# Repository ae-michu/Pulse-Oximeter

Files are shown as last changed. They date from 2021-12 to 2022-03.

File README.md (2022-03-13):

# Pulse-Oximeter
Handheld, battery powered device for measuring heart BPM and blood-oxygen content with full custom PCB design, interface design and housing.

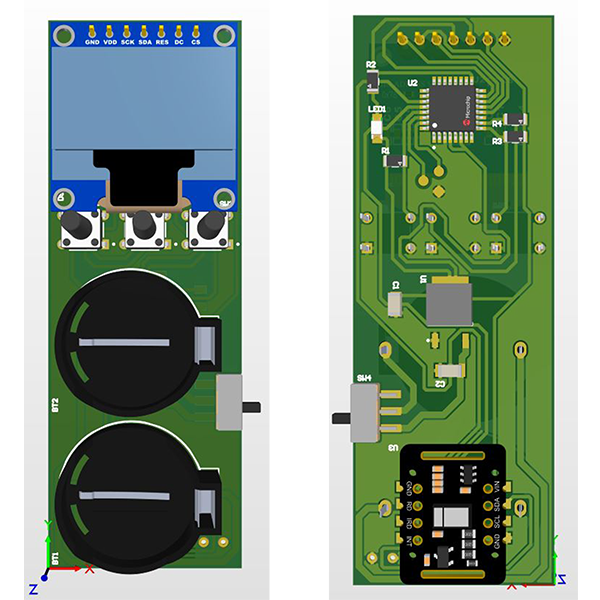
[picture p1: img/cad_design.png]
PCB CAD Design


## Introduction
It was created as a team project for a microprocessor controllers class at our university. The goal was to create a device that utilizes microcontrollers and at least 3 built-in interfaces.

## Parameters
* 3.3V power, by using two CR2032 coin cell batteries
* ATMega328p-AU with internal 8MHz clock
* MAX30102 I2C Sensor for measuring bpms and blood-oxygen levels
* 0.96" OLED SPI Display

## Working principles (and design choices)

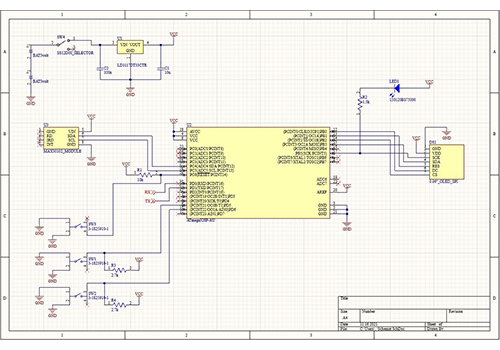
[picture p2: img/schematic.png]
Electrical schematic


### Power
Device is powered by two 3V CR2032 batteries connected in series. To sustain 3.3V the batteries were connected to LD1117-3.3 fixed voltage reagulator.

### Bootloader
Due to 3.3V power supply and according to the documentation the chips oscillator had to be lowered from 16Mhz to 8Mhz. To save space on the PCB and also lower the cost of the device we choose to flash a new bootlader that enabled the internal 8Mhz oscillator.

### BPM measurement
To achieve fast readouts and not compromise accuracy we chose to increase the amount of samples (used to calculate the moving average) with time. This gives us very fast printout of the first readings and increases accuracy with the time of measurement.

### Splash screen animation
To add some life to our interface we decided to add a splash screen animation that plays everytime the device is turned on. Each frame of the animation is stored as a bitmap. Unfortunately loading all frames from program memory caused long boot time after the device was turned off for a while (week).

### PCB
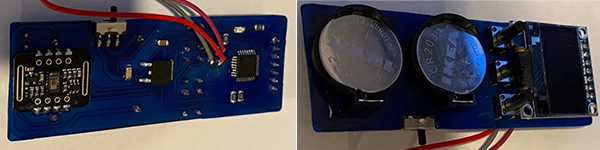
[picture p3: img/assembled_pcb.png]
Assembled PCB


It wasn't in the requirements for the project but we decided to create a pcb for the device which allowed us to use SMD components and minify the size of the product. It was designed using Altium Designer and home-etched using B327 eatching solution. Toner transfer, before etching, was done using a solution of 70% rubbing alcohol and 30% acetone. To avoid solder briding and shorts uv curable solder mask was also put on.

### Enclousure
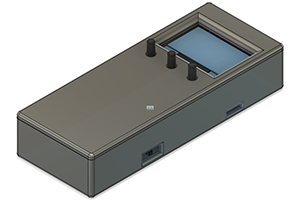
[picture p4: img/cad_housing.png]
Housing


Enclousure was designed in Fusion 360 and 3D printed using white PLA fillament. It was desinged around CAD files of the pcb.

## Team
<table>
<td align="center"><a href="https://github.com/ae-michu"><br /><sub><b>Michał Pękal</b></sub></a><br /><p style="font-size:12px">Electronics Design<br> Firmware</p></td>

<td align="center"><a href="https://github.com/olafka0"><br /><sub><b>Oliwia Wawrzyniak</b></sub></a><br /><p style="font-size:12px">UX/UI Design<br><br></p></td>

<td align="center"><a href="https://github.com/pablithone"><br /><sub><b>Paweł Lewandowski</b></sub></a><br /><p style="font-size:12px">Enclousure Design<br><br></p></td>
</table>

<br>
<br>
<br>

### Legal note
THE SOFTWARE, HARDWARE DESIGN ARE PROVIDED “AS IS”, WITHOUT WARRANTY OF ANY KIND, EXPRESS OR IMPLIED, INCLUDING BUT NOT LIMITED TO THE WARRANTIES OF MERCHANTABILITY, FITNESS FOR A PARTICULAR PURPOSE AND NONINFRINGEMENT. IN NO EVENT SHALL THE AUTHORS OR COPYRIGHT HOLDERS BE LIABLE FOR ANY CLAIM, DAMAGES OR OTHER LIABILITY, WHETHER IN AN ACTION OF CONTRACT, TORT OR OTHERWISE, ARISING FROM, OUT OF OR IN CONNECTION WITH THE SOFTWARE AND HARDWARE DESIGN OR THE USE OR OTHER DEALINGS IN THE SOFTWARE AND HARDWARE DESIGN.

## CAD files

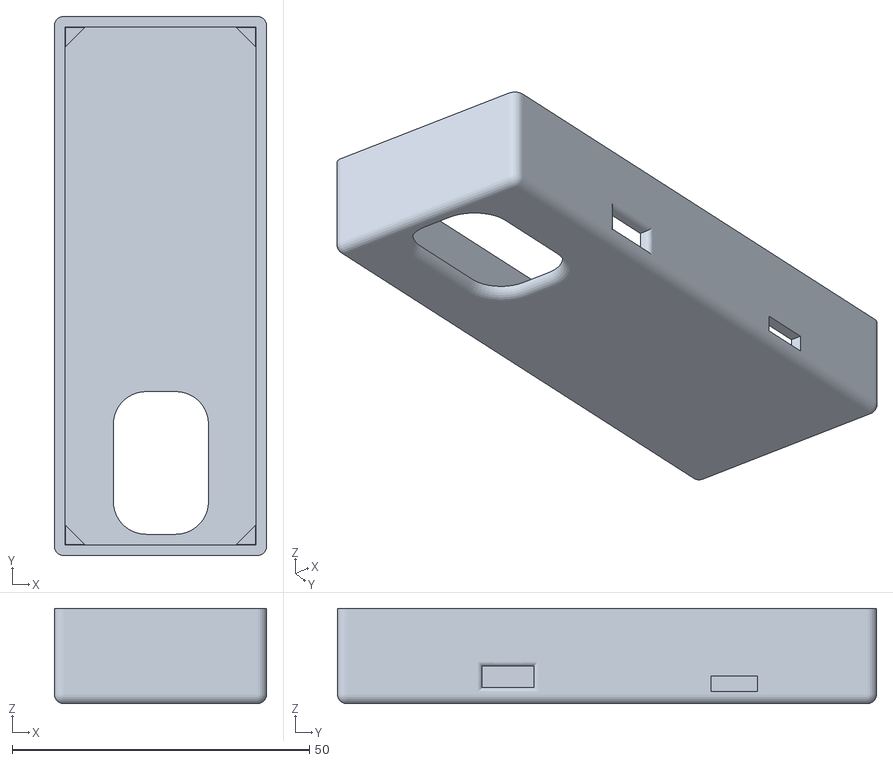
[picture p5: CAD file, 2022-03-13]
CAD/housing/main_housing.stl
35.7 x 90.7 x 16.0

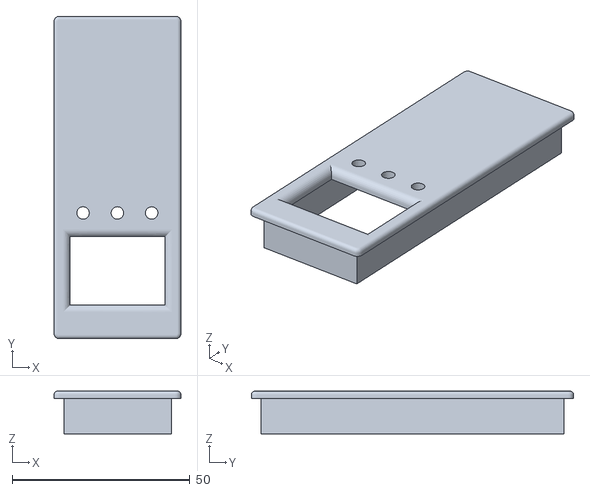
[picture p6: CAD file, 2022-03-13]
CAD/housing/top_cover.stl
35.7 x 90.6 x 12.0

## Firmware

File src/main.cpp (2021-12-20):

#include <Arduino.h>
#include <display.h>
#include <sensor.h>

// #define DEBUG                    // uncomment to enable writing data to monitor

#define BUTTON1         5           // pin number of first button (bpm)
#define BUTTON2         6           // pin number of second button (o2)

#define DISPLAY_DC      8           // pin number od display dc pin
#define DISPLAY_CS      10          // pin number of display cs pin
#define DISPLAY_RESET   9           // pin number of display reset pin

// init display and sensor objects
Display display(U8G2_R0, DISPLAY_CS, DISPLAY_DC, DISPLAY_RESET);
Sensor sensor;

// set global variables
bool screen = false;              // false - bpm screen, true - o2 screen
bool changeScreenFlag = true;     // false when screen change should occur
int lastBpm = 0;                  // store last bpm value
int lastO2 = 0;                   // store last o2 value

void setup() {

  #ifdef DEBUG
    Serial.begin(115200);
  #endif

  // set buttons as inputs
  pinMode(BUTTON1, INPUT);
  pinMode(BUTTON2, INPUT);

  // start display and clear it
  display.begin();
  display.clearDisplay();

  display.startAnimation();      // display splash animation

  display.clearDisplay();
  sensor.init();                // start sensor
}

void loop() {
  // detect if button was pressed, if so then set screen flag corresponding to button pressed
  // and set changeScreenFlag to signalize that screen change should occur 
  if (!digitalRead(BUTTON1)) {
    if (screen) {
      screen = false;
      changeScreenFlag = true;
    }
  }

  if (!digitalRead(BUTTON2)) {
    if (!screen) {
      screen = true;
      changeScreenFlag = true;
    }
  }

  // change screens when changeScreenFlag is set, and reset the flag
  if (changeScreenFlag) {
    changeScreenFlag = false;

    display.firstPage();
    do {
      if (!screen) {
        display.drawBPMScreen();
        display.drawBPMValue(0);
      } else {
        display.drawO2Screen();
      }
    } while (display.nextPage());
  }

  #ifdef DEBUG
    float bpmData = sensor.getBPMData();
    float o2Data = sensor.getO2Data();
  #endif

  #ifndef DEBUG
    sensor.getBPMData();
    sensor.getO2Data();
  #endif

  // display values based on selected screen
  if (!screen) {
    float bpm = sensor.getBPM();

    if (((int)bpm != lastBpm) && ((int)bpm != NAN)) {
      lastBpm = (int)bpm;

      display.firstPage();
      do {
        display.drawBPMScreen();
        display.drawBPMValue((int)bpm);
      } while (display.nextPage());
    }

    #ifdef DEBUG
      Serial.print("bpmData: ");
      Serial.print(bpmData);
      Serial.print(", bpm: ");
      Serial.println(bpm);
    #endif
  } else {
    float o2 = sensor.getO2();

    if (((int)o2 != lastO2) && ((int)o2 >= 0)) {
      lastO2 = (int)o2;

      display.firstPage();
      do {
        display.drawO2Screen();
        display.drawO2Value((int)o2);
      } while (display.nextPage());
    }

    #ifdef DEBUG
      Serial.print("o2Data: ");
      Serial.print(o2Data);
      Serial.print(", o2: ");
      Serial.println(o2);
    #endif
  }

  delay(10);
}
